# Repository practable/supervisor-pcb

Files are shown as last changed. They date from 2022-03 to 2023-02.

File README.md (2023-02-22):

# Remote Labs Supervisor PCB V1.2

## Project Brief - [Remote Labs Supervisor PCB V1.2]
Design a PCB to provide power to remote labs experiments, which involve students programming microcontrollers remotely. PCB should also provide a supervisory role, blocking actuation of experimental hardware if it is likely to cause damage to the equipment. <br> <br>

This allows students to upload their own code to a bare bones microcontroller, without risk of causing hardware damage or unsafe conditions. <br>
RemoteLabsSupervisorPCBV1 0_3DModel 

# Using Remote Labs Supervisor PCB 

_This document is intended to be a useage guide for the Remote Labs Supervisor PCB, and document the different use cases and configurations it is capable of._

For coded examples of the various features please see [PCB Unit Tests](https://github.com/ImogenWren/RemoteLabs_Supervisor_PCB/tree/main/Verification%20Tests/PCB%20Unit%20Tests), which contains
arduino code firmware used during testing all hardware features of the PCB.

For the purposes of this document, it is assumed that the Motherboard PCB is populated with both Arduino Nano IoT 33 Daughterboards __(A1 & A2)__, with shift registers installed, and NOT the bare bones SAMD21 MCU.
A seperate document will be provided for cases in which SAMD21 MCUs are mounted to the motherboard directly.

### Pin Naming and Shift Registers

_All MCU pins will be referenced by the Arduino Pin Numbers in this document. 
Additional pins are sourced via Shift Registers attached to each MCU.
Shift Register pins are labelled as Q0 - Q7.
Both MCU connections to their independent shift registers are detailed below._

MCU Pin |  Shift Register Function 	|
---		| ---						|
D8		| LATCH	(Write to Register)	|
D11		| MOSI (Data)				|
D13		| SCK						|

_Complete pinout diagrams for both MCUs and Shift Registers can be found at the bottom of this document_

### Powering the System

The System should be provided 12v DC power via the yellow XT60 connector __J3__. The system is specified to draw a maximum of ~ 8A depending on experiment configuration, ensure that power supply selected is sufficient for specific use case.

Diode D6 (Blue) will light to show correct polarity power is provided to input.
Diode D7 (Orange) will light to show 3V3 DC power is available to microcontrollers and periferal devices.

Motherboard has reverse polarity protection, however care should be taken to ensure correct orientation of power input. - NOTE: Currently missing protection diode- awaiting delivery

### Programming the MCUs

Each MCU, supervisor and student are able to be programmed via the USB connector on the daughterboard, or via UART using the 5 pin headers __J26 Student_Prog_Header__, and __J1 Super_Prog_header__.

For UART Programming, a hat is provided for raspi GPIO pins. 5 pin cable should be connected from Raspi hat to UART Programming connector on motherboard.

__The USB connectors mounted to the __Motherboard__ should not be used if Arduino Development boards are installed, and are UNTESTED for use with bare bones MCUs installed__

-----

## Use Case 1 [Spinner Experiment]

_In this configuration the following modules should be mounted to the motherboard:_

- Infineon DC Motor Control Shield - A3

_In this configuration the following external hardware should be connected as follows:_

- DC Motor, wired to the OUTER two pins on __J18 DC Motor Output__
- Optical Encoder, plugged into __J25 Optical Encoder__

### Using the DC Motor

DC Motor PWM is routed to Infineon DC Motor Controller module via the following logic:



If MOTOR_DIR_A is driven HIGH, PWM is routed from STUDENT_MOTOR_PWM or SUPERVISOR_MOTOR_PWM to MOTOR_OUT_1
If MOTOR_DIR_B is driven HIGH, PWM is routed from STUDENT_MOTOR_PWM or SUPERVISOR_MOTOR_PWM to MOTOR_OUT_2

Care must be taken to avoid driving MOTOR_DIR_A and MOTOR_DIR_B to HIGH at the same time as this will cause shoot through.

In Order to avoid shoot through condition, Student does not have direct input to MOTOR_DIR_A or MOTOR_DIR_B. These outputs are spoofed via the Supervisor MCU.

The MCU able to pass PWM signal to Motor Control Module is selected by MCU_MOTOR_SELECT pin. When HIGH - STUDENT_MOTOR_PWM is active, when LOW - SUPERVISOR_MOTOR_PWM is active.

In order to enable the DC Motor Control Module, OUT_M_ENABLE must also be set HIGH. This is routed from either MCU using the same logic as above, when MCU_MOTOR_SELECT is HIGH, ENABLE is routed from STUDENT_MOTOR_EN, when it is set LOW, ENABLE is routed from SUPERVISOR_MOTOR_EN.

M_I_SENSE_1 and M_I_SENSE_2 output is buffered and distributed to both MCUs.

### Supervisor MCU

Supervisor MCU uses the following table for DC Motor Control:

MCU 		|Pin 	| Pin Name 		| State 		| Motor Behaviour 		| Notes
---			|---	|---			|---			|---					|---
SUPERVISOR 	|D12 	|MOTOR_DIR_1	| HIGH or LOW	| Sets motor Direction	| IF(D7 == HIGH){D12 MUST = LOW)
SUPERVISOR	|D7		|MOTOR_DIR_2	| LOW or HIGH 	| Sets motor Direction 	| IF(D12 == HIGH){D7 MUST = LOW)
SUPERVISOR	|Q0		|DC_MOTOR_EN	| HIGH			| Enables DC Motor Drive|
SUPERVISOR	|Q1		|STUDENT_M_EN	| LOW			| Blocks Student Control, Enables Supervisor Control| 
SUPERVISOR	|A7		|DC_MOTOR_IS1	| ANALOG INPUT	| Current Draw and Fault Condition Detection| 
SUPERVISOR	|A6		|DC_MOTOR_IS2	| ANALOG INPUT	| Current Draw and Fault Condition Detection| 

### Student MCU

Student MCU uses the following table for DC Motor Control: *Note - Student control relys on specific pin configurations of Supervisor MCU*

MCU 		|Pin 	| Pin Name 		| State 		| Motor Behaviour 		| Notes
---			|---	|---			|---			|---					|---
STUDENT 	|D12 	|MOTOR_DIR_1	| HIGH or LOW	| Detected by Supervisor PIN A1	| IF(D7 == HIGH){D12 MUST = LOW)
STUDENT		|D7		|MOTOR_DIR_2	| LOW or HIGH 	| Detected by Supervisor PIN A0	| IF(D12 == HIGH){D7 MUST = LOW)
STUDENT		|Q0		|DC_MOTOR_EN	| HIGH			| Enables DC Motor Drive|
SUPERVISOR	|Q1		|STUDENT_M_EN	| HIGH			| Blocks Supervisor Control, Enables Student Control| 
SUPERVISOR	|A1		|STDNT_DC_M_DIR_1| DIGITAL INPUT| Detects state of Student Direction Pin and Spoofs output if logic != illegal
SUPERVISOR	|A0		|STDNT_DC_M_DIR_2| DIGITAL INPUT| Detects state of Student Direction Pin and Spoofs output if logic != illegal
SUPERVISOR 	|D12 	|MOTOR_DIR_1	| HIGH or LOW	| Sets motor Direction - Spoofed from A1	| 
SUPERVISOR	|D7		|MOTOR_DIR_2	| LOW or HIGH 	| Sets motor Direction - Spoofed from A0	| 
STUDENT		|A7		|DC_MOTOR_IS1	| ANALOG INPUT	| Current Draw and Fault Condition Detection| 
STUDENT		|A6		|DC_MOTOR_IS2	| ANALOG INPUT	| Current Draw and Fault Condition Detection| 

### Using the Optical Encoder

_Optical encoder signals are buffered and provided to both MCUs simaltaniously, therefore getting useful data from Optical Encoder is the same process for both MCUs_

MCUs use the following table for Optical Encoder detection:

MCU 		|Pin 	| Pin Name 		| State 								| Notes
---			|---	|---			|---									|---
Both	 	|D2 	|ENCODER_B		| EXTERNAL INTERRUPT / DIGITAL INPUT	| For best performance, External Interrupt used for edge detection of Encoder waveform
Both		|D3		|ENCODER_A		| EXTERNAL INTERRUPT / DIGITAL INPUT 	| Alternative pin for External Interrupt.
Both		|D4		|ENCODER_INDEX	| DIGITAL INPUT							| Used to track center detent of optical encoder (Untested in software)

-----

## Use Case 2 [Governer Experiment]

In this configuration the following modules should be mounted to the motherboard:

- Infineon DC Motor Control Shield 	- A3
- DRV8825 Stepper Motor Driver		- A4

___DC Motor & Optical Encoder are accessed as Use Case 1 above___

In this configuration the following external hardware should be connected as follows:

- DC Motor, wired to the OUTER two pins on __J18 DC Motor Output__
- Stepper Motor, plugged into __J19 Stepper Motor Output__
- Optical Encoder, plugged into __J25 Optical Encoder__
- Limit Switch, plugged into __J23 limit_switch_A__

### Using the Stepper Motor

Stepper Motor Driver inputs are routed via the following logic:



When MCU_STEP_SELECT is HIGH, inputs are routed from STUDENT MCU. When MCU_STEP_SELECT is LOW, inputs are routed from SUPERVISOR MCU.

STEPP_EN is driven from Supervisor MCU Only, however does not seem to have any effect on stepper motor function. - Requires further investigation.

STEPPR_FAULT output is buffered and distributed to both MCUs.

LIMIT_1 Limit switch input is buffered and distributed to both MCUs.

### Supervisor MCU

Supervisor MCU uses the following table for Stepper Motor Control:

MCU 		|Pin 	| Pin Name 		| State 		| Motor Behaviour 									| Notes
---			|---	|---			|---			|---												|---
SUPERVISOR 	|D6 	|STEPP_STEP		| PULSE			| Motor advances 1 step per pulse					| 
SUPERVISOR	|Q2		|STUDENT_STEP_EN| LOW			| Blocks Student Control, Enables Supervisor Control| 
SUPERVISOR	|Q4		|STEPP_DIR		| HIGH or LOW	| Sets Stepper Motor Direction						|
SUPERVISOR	|Q5		|STEPP_SLP		| HIGH or LOW	| Enables and Sleeps motor to avoid overheating 	| MUST BE HIGH? to enable					| 
SUPERVISOR	|Q6		|STEPP_RST		| HIGH or LOW	| Resets controller board after fault condition 	| MUST BE HIGH? to enable					| 
SUPERVISOR	|Q7		|STEPP_EN		| HIGH or LOW	| Enables motor driver board						| NO DECERNABLE EFFECT? - Needs Testing		| 
SUPERVISOR	|A5		|STEPP_FLT		| DIGITAL INPUT	| Fault reporting from Stepper Control daughterboard| HIGH = NO FAULT, LOW = FAULT 				| 
SUPERVISOR	|A4		|LIMIT_1		| DIGITAL INPUT	| Limit Switch Detection.							| LOW = Switch Pressed 						| 

### Student MCU

Student MCU uses the following table for Stepper Motor Control: *Note - Student control relys on specific pin configurations of Supervisor MCU*

MCU 		|Pin 	| Pin Name 		| State 		| Motor Behaviour 									| Notes
---			|---	|---			|---			|---												|---
STUDENT 	|D6 	|STEPP_STEP		| PULSE			| Motor advances 1 step per pulse					| 
SUPERVISOR	|Q2		|STUDENT_STEP_EN| HIGH			| Enables Student Control, Blocks Supervisor Control| 
STUDENT 	|Q4		|STEPP_DIR		| HIGH or LOW	| Sets Stepper Motor Direction						|
STUDENT		|Q5		|STEPP_SLP		| HIGH or LOW	| Enables and Sleeps motor to avoid overheating 	| MUST BE HIGH? to enable					| 
STUDENT		|Q6		|STEPP_RST		| HIGH or LOW	| Resets controller board after fault condition 	| MUST BE HIGH? to enable					| 
SUPERVISOR	|Q7		|STEPP_EN		| HIGH or LOW	| Enables motor driver board						| NO DECERNABLE EFFECT? - Needs Testing		| 
STUDENT		|A5		|STEPP_FLT		| DIGITAL INPUT	| Fault reporting from Stepper Control daughterboard| HIGH = NO FAULT, LOW = FAULT 				| 
STUDENT		|A4		|LIMIT_1		| DIGITAL INPUT	| Limit Switch Detection.							| LOW = Switch Pressed 						|

#### Additional Stepper Motor Functions

SW1 - Stepper Mode Dipswitches set number of steps per revolution. If UNPOPULATED setting is at MAX RESOLUTION. (1, 1, 1 ) logic for MODE inputs.

-----

## Use Case 3 [Digger Experiment]

In this configuration the following modules should be mounted to the motherboard:

- Infineon DC Motor Control Shield 	- A3

___DC Motor & Optical Encoder are accessed as Use Case 1 above___

In this configuration the following external hardware should be connected as follows:

- DC Motor, wired to the OUTER two pins on __J18 DC Motor Output__
- Optical Encoder, plugged into __J25 Optical Encoder__
- Limit Switch, plugged into __J23 limit_switch_A__
- Servo, plugged into __J20 Servo_A__

In this use case, supervisor must calibrate and track the position of DC motor to avoid equipment collision with self. 

### Supervisor MCU

Supervisor has ultimate control of the Servo PPM output.

Supervisor MCU uses the following table for Servo Motor Control:

MCU 		|Pin 	| Pin Name 		| State 		| Motor Behaviour 									| Notes
---			|---	|---			|---			|---												|---
SUPERVISOR 	|D9 	|SERVO_1		| PPM Output	| PPM Standard sets Servo Position					| 

### Student MCU

Student MCU has no direct output to servo_1, instead supervisor must spoof and constrain output;
given either a PWM signal, or PPM signal from the Student, applied to __Pin A2__ of the supervisorU MCU.

Student MCU uses the following table for Servo Motor Control: *Note - Student control relys on specific pin configurations of Supervisor MCU*

MCU 		|Pin 	| Pin Name 		| State 		| Motor Behaviour 									| Notes
---			|---	|---			|---			|---												|---
STUDENT 	|D9 	|SERVO_1		| PPM or PWM Output	| PPM/PWM used to infer desired position of servo	| 
SUPERVISOR	|A2		|STDNT_SRVO_RX_1| ANALOG INPUT or EXTERNAL INTERRUPT	| Detects infered desired position for servo| 
SUPERVISOR 	|D9 	|SERVO_1		| PPM Output	| PPM Standard sets Servo Position					| 

-----

## Use Case 4 [Pendulum Experiment]

*NOTE: USE CASE UNTESTED*

In this configuration the following modules should be mounted to the motherboard:

- Remote Labs Pendulum PCB Daughterboard - A3

In this configuration the following external hardware should be connected as follows:

- Pendulum Driver, wired to the OUTER two pins on __J18 DC Motor Output__
- Optical Encoder, plugged into __J25 Optical Encoder__

### Supervisor MCU

Supervisor MCU uses the following table for Pendulum Control:

MCU 		|Pin 	| Pin Name 		|Pendulum PCB Pin Name	| State 		| Pendulum Behaviour 	| Notes
---			|---	|---			|---					|---			|---					|---
SUPERVISOR 	|Q0		|DC_MOTOR_EN	| ENABLE	| DIGTAL OUTPUT	| Drive	 |Tried to avoid this being on a shift register - failed can it be moved to another pin? User Thermo A3, and enable
SUPERVISOR 	|D6		|STEPP_STEP		| PENDULUM_PIN_1		| DIGTAL OUTPUT	| Load					|  
SUPERVISOR 	|D12	|DC_MOTOR_DIR_1	| PENDULUM_PIN_7		| DIGTAL OUTPUT	| LED_1 Control			| 	
SUPERVISOR 	|D7		|DC_MOTOR_DIR_2	| PENDULUM_PIN_8		| DIGTAL OUTPUT	| LED_2 Control			| 
SUPERVISOR 	|D9		|SERVO_1		| PENDULUM_PIN_6		| DIGTAL OUTPUT	| LED_3 Control			| 
SUPERVISOR 	|Q1		|STUDENT_M_EN	| PENDULUM_PIN_2		| LOW			| Blocks Student Control, Enables Supervisor Control |
SUPERVISOR	|A7		|DC_MOTOR_IS1	| I_SENSE_1				| ANALOG INPUT	| Current Draw and Fault Condition Detection|  Check which way around these are
SUPERVISOR	|A6		|DC_MOTOR_IS2	| I_SENSE_2				| DIGITAL INPUT	| Current SIGN reporting (+/-)| HIGH = Positive Current, LOW = Negative Current

### Student MCU

Student MCU uses the following table for Stepper Motor Control: *Note - Student control relys on specific pin configurations of Supervisor MCU*

MCU 		|Pin 	| Pin Name 		|Pendulum PCB Pin Name	| State 		| Pendulum Behaviour 	| Notes
---			|---	|---			|---					|---			|---					|---
STUDENT 	|Q0		|DC_MOTOR_EN	| ENABLE	| DIGTAL OUTPUT	| Drive	 |Tried to avoid this being on a shift register - failed can it be moved to another pin? User Thermo A3, and external enable
STUDENT 	|D6		|STEPP_STEP		| PENDULUM_PIN_1		| DIGTAL OUTPUT	| Load					|  
STUDENT  	|A0		|SPARE_0		| PENDULUM_PIN_3		| DIGTAL OUTPUT	| LED_1 Control			| 	
STUDENT  	|A1		|SPARE_1 		| PENDULUM_PIN_4		| DIGTAL OUTPUT	| LED_2 Control			| 
STUDENT  	|A2		|SPARE_2		| PENDULUM_PIN_5		| DIGTAL OUTPUT	| LED_3 Control			| 
SUPERVISOR 	|Q1		|STUDENT_M_EN	| PENDULUM_PIN_2		| HIGH			| Enables Student Control, Blocks Supervisor Control |
STUDENT		|A7		|DC_MOTOR_IS1	| I_SENSE_1				| ANALOG INPUT	| Current Draw and Fault Condition Detection|  Check which way around these are
STUDENT		|A6		|DC_MOTOR_IS2	| I_SENSE_2				| DIGITAL INPUT	| Current SIGN reporting (+/-)| HIGH = Positive Current, LOW = Negative Current

-----

## Additional Features

### WS2812 LEDs

To use WS2812 LED strips with any configuration, the following external hardware should be connected as follows:

- WS2821B LED Strip, connected to __J24 WS2812B LEDs__

__Supervisor MCU__ uses the following table for WS2812B LED Control.

MCU 		|Pin 	| Pin Name 		| State 		| Use			 				| Notes
---			|---	|---			|---			|---							|---
SUPERVISOR 	|D5 	|PIXEL_DATA		| DIGITAL OUTPUT| Sets LED Colour & Brightness	|
SUPERVISOR	|Q3		|STUDENT_PIXEL_EN| LOW			| Blocks Student Control, Enables Supervisor Control		|

__Student MCU__ uses the following table for WS2812B LED Control.: *Note - Student control relys on specific pin configurations of Supervisor MCU*

MCU 		|Pin 	| Pin Name 		| State 		| Use			 				| Notes
---			|---	|---			|---			|---							|---
STUDENT		|D5 	|PIXEL_DATA		| DIGITAL OUTPUT| Sets LED Colour & Brightness	|
SUPERVISOR	|Q3		|STUDENT_PIXEL_EN| HIGH			| Enables Student Control, Blocks Supervisor Control		|

### Power Output Connectors

| Voltage/Bus 		| Purpose/Name	| Component Number 	| Connector Type 	| Current Considerations 	|
|---				|---			|---				|---				|---						|
| 12V				| 12V_DC		|		J30			| Screw Terminal	| Unregulated ~8A Max(For entire Bus)|
| 12V				| Strip Lighting| 		J4			| Molex				| Unregulated ~8A Max(For entire Bus)|
| 12V       		| DC MOTOR PWR	|		J16			| Screw Terminal	| Unregulated ~8A Max(For entire Bus)|
| 5V_DC_LED			| 5V_DC_LED		| 		J6			| Screw Terminal	| 1A Total. Regulated	|
| 5V_DC_RPI			| 5V_DC Spare	| 		J31			| Screw Terminal	| 2.5A Total. Regulated	|
| 5V_DC_RPI			| USB Power		| 		J5			| USB A Socket x2	| 2.5A Total. Regulated	|

#### Additional Voltage Bus Connections

Additional headers have been provided for:
- 3V3 DC Power Output (1A Max)
- 5V DC Digital Power Output (2 - 2.5A Max, including USB Socket)
- 5V DC Servo Power Output (1A Max)
- 12V DC Bus (Unregulated - 6A Max)

These are intended for future use, fault finding or reconfirging PCBs to perform tasks outside of the specified use cases.

### Thermocouple

__Currently Unavailable due to parts shortages__

To use Thermocouple Input with any configuration, the following external hardware should be connected as follows:

- K-Type Thermocouple, connected to __J22 Thermocouple__ connector.

__Thermocouple input __J22 Thermocouple__ requires IC __U19 AD8497__ To be populated. (UNTESTED)__

Analog voltage is buffered and distributed to both MCUs, __Pin A3__

## Pinout Diagrams

_MCU and Shift Register Pinout diagrams_

##### Supervisor MCU



##### Student MCU



## CAD Renders

RemoteLabs Supervisor PCBV1 0 CAD Design
RemoteLabsSupervisorPCBV1 0_3DModel_3


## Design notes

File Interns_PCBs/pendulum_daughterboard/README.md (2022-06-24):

# Pendulum Driver Daughterboard

The task is to design and fabricate a drop in replacement for the motor driver board on the new remote labs PCB. The original daughterboard is the Infineon motor control shield:
  https://uk.rs-online.com/web/p/shields-for-arduino/

The new PCB will be driving the pendulum experiment, the circuit and experiment is documented in this github repo:
https://github.com/practable/penduino

Pendulum Driver Origional Circuit

RL supervisor PCB repo found at:
https://github.com/ImogenWren/RemoteLabs_Supervisor_PCB

### Schematic Showing connections to motherboard
 Infineon Motor Driver Connections to motherboard

I have created a folder for the pendulum daughterboard, if you could keep all the KiCAD files and any notes you make in this folder. Part of the reasoning of this project is “showing our working” so documenting any design decisions you make, current draw calculations, trace sizes etc would be valuable.

The new daughterboard needs to fit into the slot for the old daughterboard, and must match its pinout. We have 3 digital inputs available to the daughterboard, ENABLE, IN_1 and IN_2 and 2 Analog outputs from the daughterboard. The analog outputs go through a set of buffers to feed the ADC pins on each MCU, and both have a 470r resistor to GND. 

On the schematic it shows 4 digital inputs, so I would have a quick chat with Tim Drysdale (CCed In) and ask him if we can tie the two LEDs to the drive and the load pin. This means we would have 2 digital inputs, and one spare. Don’t worry about the encoder as that plugs directly into the motherboard and doesn’t need any additional work.

I don’t know if it is required, but it might be worthwhile thinking about adding some kind of current sensing to the daughterboard which can be output on the analog pins. This could be via a current sense IC, or some other method. It would likely need to measure current through the coil in both directions, but this is a stretch goal. The important part is just replicating the function of the existing circuit. Whatever method is chosen, make sure that the parts to complete are available and in stock from UK suppliers.

Power input into the daughterboard – unfortunately I didn’t think of putting 5v on any of the spare pins, however there is a 5v header on the motherboard, so we will run a wire from here into a large 5v Vin pin on your daughterboard. The coil connections will come out on 2 large pads, like the motor driver board and this will be wired to the screw terminals on the motherboard. These are shown as dotted lines on the picture above.

Ideally this should be a 2 layer board to allow us to fabricate a prototype in house.

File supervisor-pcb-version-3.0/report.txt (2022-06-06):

Info: Processing symbol 'A1:Module:Arduino_Nano'.
Info: Processing symbol 'A2:Module:Arduino_Nano'.
Info: Processing symbol 'A3:Module:Infineon Motor Sheild hiddenPins'.
Info: Processing symbol 'A4:Module:DRV8825 Stepper Motor Module'.
Info: Processing symbol 'A5:Module:LM2596S DC-DC Module'.
Info: Processing symbol 'C1:Capacitor_SMD:C_0805_2012Metric_Pad1.18x1.45mm_HandSolder'.
Info: Processing symbol 'C1A1:Capacitor_SMD:C_0805_2012Metric_Pad1.18x1.45mm_HandSolder'.
Info: Processing symbol 'C1B1:Capacitor_SMD:C_0805_2012Metric_Pad1.18x1.45mm_HandSolder'.
Info: Processing symbol 'C2:Capacitor_SMD:C_0805_2012Metric_Pad1.18x1.45mm_HandSolder'.
Info: Processing symbol 'C2A1:Capacitor_SMD:C_0805_2012Metric_Pad1.18x1.45mm_HandSolder'.
Info: Processing symbol 'C2B1:Capacitor_SMD:C_0805_2012Metric_Pad1.18x1.45mm_HandSolder'.
Info: Processing symbol 'C3:Capacitor_SMD:C_0805_2012Metric_Pad1.18x1.45mm_HandSolder'.
Info: Processing symbol 'C4:Capacitor_SMD:C_0805_2012Metric_Pad1.18x1.45mm_HandSolder'.
Info: Processing symbol 'C5:Capacitor_SMD:C_0805_2012Metric_Pad1.18x1.45mm_HandSolder'.
Info: Processing symbol 'C6:Capacitor_SMD:C_0805_2012Metric_Pad1.18x1.45mm_HandSolder'.
Info: Processing symbol 'C7:Capacitor_Tantalum_SMD:CP_EIA-2012-12_Kemet-R_Pad1.30x1.05mm_HandSolder'.
Info: Processing symbol 'C8:Capacitor_SMD:C_0805_2012Metric_Pad1.18x1.45mm_HandSolder'.
Info: Processing symbol 'C9:Capacitor_SMD:C_0805_2012Metric_Pad1.18x1.45mm_HandSolder'.
Info: Processing symbol 'C10:Capacitor_SMD:C_0805_2012Metric_Pad1.18x1.45mm_HandSolder'.
Info: Processing symbol 'C11:Capacitor_SMD:C_0805_2012Metric_Pad1.18x1.45mm_HandSolder'.
Info: Processing symbol 'C12:Capacitor_SMD:C_0805_2012Metric_Pad1.18x1.45mm_HandSolder'.
Info: Processing symbol 'C13:Capacitor_SMD:C_0805_2012Metric_Pad1.18x1.45mm_HandSolder'.
Info: Processing symbol 'C14:Capacitor_SMD:C_0805_2012Metric_Pad1.18x1.45mm_HandSolder'.
Info: Processing symbol 'C15:Capacitor_SMD:C_0805_2012Metric_Pad1.18x1.45mm_HandSolder'.
Info: Processing symbol 'C16:Capacitor_SMD:C_0805_2012Metric_Pad1.18x1.45mm_HandSolder'.
Info: Processing symbol 'C17:Capacitor_Tantalum_SMD:CP_EIA-2012-12_Kemet-R_Pad1.30x1.05mm_HandSolder'.
Info: Processing symbol 'C18:Capacitor_SMD:C_0805_2012Metric_Pad1.18x1.45mm_HandSolder'.
Info: Processing symbol 'C19:Capacitor_SMD:C_0805_2012Metric_Pad1.18x1.45mm_HandSolder'.
Info: Processing symbol 'C20:Capacitor_SMD:C_0805_2012Metric_Pad1.18x1.45mm_HandSolder'.
Info: Processing symbol 'C21:Capacitor_SMD:C_0805_2012Metric_Pad1.18x1.45mm_HandSolder'.
Info: Processing symbol 'C22:Capacitor_SMD:C_0805_2012Metric_Pad1.18x1.45mm_HandSolder'.
Info: Processing symbol 'C23:Capacitor_SMD:C_0805_2012Metric_Pad1.18x1.45mm_HandSolder'.
Info: Processing symbol 'C24:Capacitor_SMD:C_0805_2012Metric_Pad1.18x1.45mm_HandSolder'.
Info: Processing symbol 'C25:Capacitor_SMD:C_0805_2012Metric_Pad1.18x1.45mm_HandSolder'.
Info: Processing symbol 'C26:Capacitor_SMD:C_0805_2012Metric_Pad1.18x1.45mm_HandSolder'.
Info: Processing symbol 'C27:Capacitor_SMD:C_0805_2012Metric_Pad1.18x1.45mm_HandSolder'.
Info: Processing symbol 'C28:Capacitor_SMD:C_0805_2012Metric_Pad1.18x1.45mm_HandSolder'.
Info: Processing symbol 'C29:Capacitor_SMD:C_0805_2012Metric_Pad1.18x1.45mm_HandSolder'.
Info: Processing symbol 'C30:Capacitor_SMD:C_0805_2012Metric_Pad1.18x1.45mm_HandSolder'.
Info: Processing symbol 'C31:Capacitor_SMD:C_0805_2012Metric_Pad1.18x1.45mm_HandSolder'.
Info: Processing symbol 'C32:Capacitor_SMD:C_0805_2012Metric_Pad1.18x1.45mm_HandSolder'.
Info: Processing symbol 'C33:Capacitor_SMD:C_0805_2012Metric_Pad1.18x1.45mm_HandSolder'.
Info: Processing symbol 'C34:Capacitor_SMD:C_0805_2012Metric_Pad1.18x1.45mm_HandSolder'.
Info: Processing symbol 'C35:Capacitor_SMD:C_0805_2012Metric_Pad1.18x1.45mm_HandSolder'.
Info: Processing symbol 'C36:Capacitor_SMD:C_0805_2012Metric_Pad1.18x1.45mm_HandSolder'.
Info: Processing symbol 'C38:Capacitor_SMD:C_0805_2012Metric_Pad1.18x1.45mm_HandSolder'.
Info: Processing symbol 'C39:Capacitor_SMD:C_0805_2012Metric_Pad1.18x1.45mm_HandSolder'.
Info: Processing symbol 'C40:Capacitor_SMD:C_0805_2012Metric_Pad1.18x1.45mm_HandSolder'.
Info: Processing symbol 'C41:Capacitor_SMD:C_0805_2012Metric_Pad1.18x1.45mm_HandSolder'.
Info: Processing symbol 'C42:Capacitor_SMD:C_0805_2012Metric_Pad1.18x1.45mm_HandSolder'.
Info: Processing symbol 'C43:Capacitor_SMD:C_0805_2012Metric_Pad1.18x1.45mm_HandSolder'.
Info: Processing symbol 'D1:Diode_SMD:D_MiniMELF'.
Info: Processing symbol 'D2:Diode_SMD:Nexperia_CFP3_SOD-123W'.
Info: Processing symbol 'D3:Package_TO_SOT_SMD:SOT-143'.
Info: Processing symbol 'D4:Package_TO_SOT_SMD:SOT-143'.
Info: Processing symbol 'D5:Diode_SMD:Nexperia_CFP3_SOD-123W'.
Info: Processing symbol 'D6:Diode_SMD:D_0805_2012Metric_Pad1.15x1.40mm_HandSolder'.
Info: Processing symbol 'D7:Diode_SMD:D_0805_2012Metric_Pad1.15x1.40mm_HandSolder'.
Info: Processing symbol 'D8:Diode_SMD:D_0805_2012Metric_Pad1.15x1.40mm_HandSolder'.
Info: Processing symbol 'R19:Resistor_SMD:R_0805_2012Metric_Pad1.20x1.40mm_HandSolder'.
Info: Processing symbol 'D9:Diode_SMD:D_0805_2012Metric_Pad1.15x1.40mm_HandSolder'.
Info: Processing symbol 'R20:Resistor_SMD:R_0805_2012Metric_Pad1.20x1.40mm_HandSolder'.
Info: Processing symbol 'EC1:Capacitor_SMD:CP_Elec_4x5.4'.
Info: Processing symbol 'EC2:Capacitor_SMD:CP_Elec_4x5.4'.
Info: Processing symbol 'EC3:Capacitor_SMD:CP_Elec_4x5.4'.
Info: Processing symbol 'EC4:Capacitor_SMD:CP_Elec_4x5.4'.
Info: Processing symbol 'EC5:Capacitor_SMD:CP_Elec_4x5.4'.
Info: Processing symbol 'EC6:Capacitor_SMD:CP_Elec_4x5.4'.
Info: Processing symbol 'EC7:Capacitor_SMD:CP_Elec_4x5.4'.
Info: Processing symbol 'EC8:Capacitor_SMD:CP_Elec_4x5.4'.
Info: Processing symbol 'EC9:Capacitor_SMD:CP_Elec_6.3x7.7'.
Info: Processing symbol 'EC10:Capacitor_SMD:CP_Elec_6.3x7.7'.
Info: Processing symbol 'EC11:Capacitor_SMD:CP_Elec_6.3x7.7'.
Info: Processing symbol 'EC12:Capacitor_SMD:CP_Elec_6.3x7.7'.
Info: Processing symbol 'F1:Fuse:Fuseholder_Cylinder-5x20mm_Stelvio-Kontek_PTF78_Horizontal_Open'.
Info: Processing symbol 'F2:Fuse:Fuseholder_Cylinder-5x20mm_Stelvio-Kontek_PTF78_Horizontal_Open'.
Info: Processing symbol 'FB1:Inductor_SMD:L_0805_2012Metric_Pad1.05x1.20mm_HandSolder'.
Info: Processing symbol 'FB2:Inductor_SMD:L_0805_2012Metric_Pad1.05x1.20mm_HandSolder'.
Info: Processing symbol 'H1:MountingHole:MountingHole_3.2mm_M3_Pad_Via'.
Info: Processing symbol 'R21:Resistor_SMD:R_0805_2012Metric_Pad1.20x1.40mm_HandSolder'.
Info: Processing symbol 'R22:Resistor_SMD:R_0805_2012Metric_Pad1.20x1.40mm_HandSolder'.
Info: Processing symbol 'R23:Resistor_SMD:R_0805_2012Metric_Pad1.20x1.40mm_HandSolder'.
Info: Processing symbol 'R24:Resistor_SMD:R_0805_2012Metric_Pad1.20x1.40mm_HandSolder'.
Info: Processing symbol 'R25:Resistor_SMD:R_0805_2012Metric_Pad1.20x1.40mm_HandSolder'.
Info: Processing symbol 'R26:Resistor_SMD:R_0805_2012Metric_Pad1.20x1.40mm_HandSolder'.
Info: Processing symbol 'R27:Resistor_SMD:R_0805_2012Metric_Pad1.20x1.40mm_HandSolder'.
Info: Processing symbol 'R28:Resistor_SMD:R_0805_2012Metric_Pad1.20x1.40mm_HandSolder'.
Info: Processing symbol 'R29:Resistor_SMD:R_0805_2012Metric_Pad1.20x1.40mm_HandSolder'.
Info: Processing symbol 'H2:MountingHole:MountingHole_3.2mm_M3_Pad_Via'.
Info: Processing symbol 'R30:Resistor_SMD:R_0805_2012Metric_Pad1.20x1.40mm_HandSolder'.
Info: Processing symbol 'R31:Resistor_SMD:R_0805_2012Metric_Pad1.20x1.40mm_HandSolder'.
Info: Processing symbol 'R32:Resistor_SMD:R_0805_2012Metric_Pad1.20x1.40mm_HandSolder'.
Info: Processing symbol 'R33:Resistor_SMD:R_0805_2012Metric_Pad1.20x1.40mm_HandSolder'.
Info: Processing symbol 'R34:Resistor_SMD:R_0805_2012Metric_Pad1.20x1.40mm_HandSolder'.
Info: Processing symbol 'R35:Resistor_SMD:R_0805_2012Metric_Pad1.20x1.40mm_HandSolder'.
Info: Processing symbol 'R36:Resistor_SMD:R_0805_2012Metric_Pad1.20x1.40mm_HandSolder'.
Info: Processing symbol 'R37:Resistor_SMD:R_0805_2012Metric_Pad1.20x1.40mm_HandSolder'.
Info: Processing symbol 'R39:Resistor_SMD:R_0805_2012Metric_Pad1.20x1.40mm_HandSolder'.
Info: Processing symbol 'H3:MountingHole:MountingHole_3.2mm_M3_Pad_Via'.
Info: Processing symbol 'R40:Resistor_SMD:R_0805_2012Metric_Pad1.20x1.40mm_HandSolder'.
Info: Processing symbol 'J25:Connector_Molex:Molex_KK-254_AE-6410-05A_1x05_P2.54mm_Vertical'.
Info: Processing symbol 'R41:Resistor_SMD:R_0805_2012Metric_Pad1.20x1.40mm_HandSolder'.
Info: Processing symbol 'SW1:Button_Switch_SMD:SW_DIP_SPSTx03_Slide_6.7x9.18mm_W6.73mm_P2.54mm_LowProfile_JPin'.
Info: Processing symbol 'SW2:Button_Switch_SMD:SW_Push_1P1T_NO_CK_KSC6xxJ'.
Info: Processing symbol 'SW3:Button_Switch_SMD:SW_Push_1P1T_NO_CK_KSC6xxJ'.
Info: Processing symbol 'U1:Converter_DCDC:Converter_DCDC_RECOM_R-78E-0.5_THT'.
Info: Processing symbol 'U2:Package_TO_SOT_SMD:SOT-23-5_HandSoldering'.
Info: Processing symbol 'U3:Package_TO_SOT_SMD:SOT-223-3_TabPin2'.
Info: Processing symbol 'H4:MountingHole:MountingHole_3.2mm_M3_Pad_Via'.
Info: Processing symbol 'U4:Package_DFN_QFN:QFN-48-1EP_7x7mm_P0.5mm_EP5.15x5.15mm'.
Info: Processing symbol 'U5:Package_SO:SOIC-16_3.9x9.9mm_P1.27mm'.
Info: Processing symbol 'U6:Package_DFN_QFN:QFN-48-1EP_7x7mm_P0.5mm_EP5.15x5.15mm'.
Info: Processing symbol 'U7:Package_SO:SOIC-16_3.9x9.9mm_P1.27mm'.
Info: Processing symbol 'U8:Package_SO:SOIC-14_3.9x8.7mm_P1.27mm'.
Info: Processing symbol 'U9:Package_SO:SOIC-14_3.9x8.7mm_P1.27mm'.
Info: Processing symbol 'U10:Package_SO:SOIC-14_3.9x8.7mm_P1.27mm'.
Info: Processing symbol 'U11:Package_SO:SOIC-14_3.9x8.7mm_P1.27mm'.
Info: Processing symbol 'U12:Package_SO:SOIC-14_3.9x8.7mm_P1.27mm'.
Info: Processing symbol 'H5:MountingHole:MountingHole_3.2mm_M3_Pad_Via'.
Info: Processing symbol 'U13:Package_SO:SOIC-14_3.9x8.7mm_P1.27mm'.
Info: Processing symbol 'U14:Package_SO:SOIC-14_3.9x8.7mm_P1.27mm'.
Info: Processing symbol 'U15:Package_SO:SOIC-14_3.9x8.7mm_P1.27mm'.
Info: Processing symbol 'U16:Package_SO:SOIC-14_3.9x8.7mm_P1.27mm'.
Info: Processing symbol 'U17:Package_SO:SOIC-14_3.9x8.7mm_P1.27mm'.
Info: Processing symbol 'U18:Converter_DCDC:Converter_DCDC_RECOM_R-78E-0.5_THT'.
Info: Processing symbol 'U19:Package_SO:MSOP-8_3x3mm_P0.65mm'.
Info: Processing symbol 'U20:Package_SO:SOIC-14_3.9x8.7mm_P1.27mm'.
Info: Processing symbol 'U21:Package_SO:SOIC-14_3.9x8.7mm_P1.27mm'.
Info: Processing symbol 'H6:MountingHole:MountingHole_3.2mm_M3_Pad_Via'.
Info: Processing symbol 'U22:Package_SO:SOIC-14_3.9x8.7mm_P1.27mm'.
Info: Processing symbol 'U23:Package_TO_SOT_SMD:SOT-23-5_HandSoldering'.
Info: Processing symbol 'X1:Oscillator:Oscillator_SMD_Abracon_ASE-4Pin_3.2x2.5mm'.
Info: Processing symbol 'X2:Oscillator:Oscillator_SMD_Abracon_ASE-4Pin_3.2x2.5mm'.
Info: Processing symbol 'R38:Resistor_SMD:R_0805_2012Metric_Pad1.20x1.40mm_HandSolder'.
Info: Processing symbol 'J1:Connector_Molex:Molex_KK-254_AE-6410-05A_1x05_P2.54mm_Vertical'.
Info: Processing symbol 'J2:Connector_Molex:Molex_KK-254_AE-6410-03A_1x03_P2.54mm_Vertical'.
Info: Processing symbol 'J3:Connector_AMASS:AMASS_XT60PW-M'.
Info: Processing symbol 'J4:Connector_Molex:Molex_KK-254_AE-6410-02A_1x02_P2.54mm_Vertical'.
Info: Processing symbol 'J5:Connector_USB:USB_A_Wuerth_61400826021_Horizontal_Stacked'.
Info: Processing symbol 'J6:TerminalBlock:TerminalBlock_Altech_AK300-2_P5.00mm'.
Info: Processing symbol 'J7:Connector_USB:USB_Mini-B_Lumberg_2486_01_Horizontal'.
Info: Processing symbol 'J8:Connector_PinHeader_2.54mm:PinHeader_1x08_P2.54mm_Vertical'.
Info: Processing symbol 'J9:Connector_PinHeader_2.54mm:PinHeader_1x04_P2.54mm_Vertical'.
Info: Processing symbol 'J10:Connector_PinHeader_2.54mm:PinHeader_1x08_P2.54mm_Vertical'.
Info: Processing symbol 'J11:Connector_PinHeader_2.54mm:PinHeader_1x03_P2.54mm_Vertical'.
Info: Processing symbol 'J12:Connector_PinHeader_2.54mm:PinHeader_1x08_P2.54mm_Vertical'.
Info: Processing symbol 'J13:Connector_USB:USB_Mini-B_Lumberg_2486_01_Horizontal'.
Info: Processing symbol 'J14:Connector_PinHeader_2.54mm:PinHeader_1x08_P2.54mm_Vertical'.
Info: Processing symbol 'J15:Connector_PinHeader_2.54mm:PinHeader_1x03_P2.54mm_Vertical'.
Info: Processing symbol 'J16:TerminalBlock:TerminalBlock_Altech_AK300-2_P5.00mm'.
Info: Processing symbol 'J17:TerminalBlock:TerminalBlock_Altech_AK300-3_P5.00mm'.
Info: Processing symbol 'J18:TerminalBlock:TerminalBlock_Altech_AK300-3_P5.00mm'.
Info: Processing symbol 'J19:Connector_JST:JST_XH_B4B-XH-A_1x04_P2.50mm_Vertical'.
Info: Processing symbol 'J20:Connector_PinHeader_2.54mm:PinHeader_1x03_P2.54mm_Vertical'.
Info: Processing symbol 'J21:Connector_PinHeader_2.54mm:PinHeader_1x03_P2.54mm_Vertical'.
Info: Processing symbol 'J22:TerminalBlock:TerminalBlock_Altech_AK300-2_P5.00mm'.
Info: Processing symbol 'J23:Connector_Molex:Molex_KK-254_AE-6410-02A_1x02_P2.54mm_Vertical'.
Info: Processing symbol 'J24:Connector_Molex:Molex_KK-254_AE-6410-02A_1x02_P2.54mm_Vertical'.
Info: Processing symbol 'J26:Connector_Molex:Molex_KK-254_AE-6410-05A_1x05_P2.54mm_Vertical'.
Info: Processing symbol 'J27:Connector_PinHeader_2.54mm:PinHeader_1x03_P2.54mm_Vertical'.
Info: Processing symbol 'J28:Connector_PinHeader_1.27mm:PinHeader_1x01_P1.27mm_Vertical'.
Info: Processing symbol 'J29:Connector_PinHeader_2.54mm:PinHeader_1x03_P2.54mm_Vertical'.
Info: Processing symbol 'J30:TerminalBlock:TerminalBlock_Altech_AK300-2_P5.00mm'.
Info: Processing symbol 'J31:TerminalBlock:TerminalBlock_Altech_AK300-2_P5.00mm'.
Info: Processing symbol 'J32:Connector_PinHeader_1.27mm:PinHeader_1x10_P1.27mm_Vertical'.
Info: Processing symbol 'J33:Connector_PinHeader_2.54mm:PinHeader_1x05_P2.54mm_Vertical'.
Info: Processing symbol 'J34:Connector_PinHeader_2.54mm:PinHeader_1x05_P2.54mm_Vertical'.
Info: Processing symbol 'J35:Connector_PinHeader_2.54mm:PinHeader_1x05_P2.54mm_Vertical'.
Info: Processing symbol 'J36:Connector_PinHeader_2.54mm:PinHeader_1x05_P2.54mm_Vertical'.
Info: Processing symbol 'JP1:Jumper:SolderJumper-3_P1.3mm_Bridged12_RoundedPad1.0x1.5mm'.
Info: Processing symbol 'JP2:Jumper:SolderJumper-3_P1.3mm_Bridged12_RoundedPad1.0x1.5mm'.
Info: Processing symbol 'JP3:000_Connectors_Immo:SolderJumper-3_P1.3mm_Bridged12_RoundedPad1.0x1.5mm_NumberLabels'.
Info: Processing symbol 'JP4:000_Connectors_Immo:SolderJumper-3_P1.3mm_Bridged12_RoundedPad1.0x1.5mm_NumberLabels'.
Info: Processing symbol 'JP6:000_Connectors_Immo:SolderJumper-3_P1.3mm_Bridged12_RoundedPad1.0x1.5mm_NumberLabels'.
Info: Processing symbol 'JP7:000_Connectors_Immo:SolderJumper-3_P1.3mm_Bridged12_RoundedPad1.0x1.5mm_NumberLabels'.
Info: Processing symbol 'JP9:000_Connectors_Immo:SolderJumper-2_P1.3mm_Open_Pad1.0x1.5mm'.
Info: Processing symbol 'JP10:000_Connectors_Immo:SolderJumper-2_P1.3mm_Open_Pad1.0x1.5mm'.
Info: Processing symbol 'NT1:NetTie:NetTie-2_SMD_Pad2.0mm'.
Info: Processing symbol 'NT2:NetTie:NetTie-2_SMD_Pad0.5mm'.
Info: Processing symbol 'NT4:NetTie:NetTie-2_SMD_Pad2.0mm'.
Info: Processing symbol 'Q1:Package_TO_SOT_THT:TO-220-3_Vertical'.
Info: Processing symbol 'R1:Resistor_SMD:R_0805_2012Metric_Pad1.20x1.40mm_HandSolder'.
Info: Processing symbol 'R2:Resistor_SMD:R_0805_2012Metric_Pad1.20x1.40mm_HandSolder'.
Info: Processing symbol 'R3:Resistor_SMD:R_0805_2012Metric_Pad1.20x1.40mm_HandSolder'.
Info: Processing symbol 'R4:Resistor_SMD:R_0805_2012Metric_Pad1.20x1.40mm_HandSolder'.
Info: Processing symbol 'R5:Resistor_SMD:R_0805_2012Metric_Pad1.20x1.40mm_HandSolder'.
Info: Processing symbol 'R6:Resistor_SMD:R_0805_2012Metric_Pad1.20x1.40mm_HandSolder'.
Info: Processing symbol 'R7:Resistor_SMD:R_0805_2012Metric_Pad1.20x1.40mm_HandSolder'.
Info: Processing symbol 'R8:Resistor_SMD:R_0805_2012Metric_Pad1.20x1.40mm_HandSolder'.
Info: Processing symbol 'R9:Resistor_SMD:R_0805_2012Metric_Pad1.20x1.40mm_HandSolder'.
Info: Processing symbol 'R10:Resistor_SMD:R_0805_2012Metric_Pad1.20x1.40mm_HandSolder'.
Info: Processing symbol 'R11:Resistor_SMD:R_0805_2012Metric_Pad1.20x1.40mm_HandSolder'.
Info: Processing symbol 'R12:Resistor_SMD:R_0805_2012Metric_Pad1.20x1.40mm_HandSolder'.
Info: Processing symbol 'R13:Resistor_SMD:R_0805_2012Metric_Pad1.20x1.40mm_HandSolder'.
Info: Processing symbol 'R14:Resistor_SMD:R_0805_2012Metric_Pad1.20x1.40mm_HandSolder'.
Info: Processing symbol 'R15:Resistor_SMD:R_0805_2012Metric_Pad1.20x1.40mm_HandSolder'.
Info: Processing symbol 'R16:Resistor_SMD:R_0805_2012Metric_Pad1.20x1.40mm_HandSolder'.
Info: Processing symbol 'R17:Resistor_SMD:R_0805_2012Metric_Pad1.20x1.40mm_HandSolder'.
Info: Processing symbol 'R18:Resistor_SMD:R_0805_2012Metric_Pad1.20x1.40mm_HandSolder'.
Change D8 value from LED_BUILTIN to Yellow.
Change D9 value from LED_BUILTIN to Yellow.
Change X2 value from 32.768kHz to ASEK-xxxMHz.
Change JP9 value from Reset GND to Reset Jumper.
Change J16 value from DC Motor PWR to MotorController_PWR_IP.
Change J22 value from Thermocouple to Thermocouple A.
Change J2 value from WS2821B LEDs to WS2821B Header.
Change J17 value from MotorController Output to MotorController.
Reconnect R17 pin 2 from 3V3_DC_MCU to 5V_DC_RPI.
Reconnect R19 pin 2 from 3V3_DC_MCU to 5V_DC_RPI.
Change JP10 value from RESET_gnd to Reset Jumper.
Reconnect J25 pin 5 from 3V3_DC_MCU to 5V_DC_RPI.
Reconnect R21 pin 2 from 3V3_DC_MCU to 5V_DC_RPI.
Change X1 value from 32.768KhZ to ASEK-xxxMHz.
Warning: No net found for symbol H2 pin 1.
Warning: No net found for symbol H2 pin 1.
Warning: No net found for symbol H2 pin 1.
Warning: No net found for symbol H2 pin 1.
Warning: No net found for symbol H2 pin 1.
Warning: No net found for symbol H2 pin 1.
Warning: No net found for symbol H3 pin 1.
Warning: No net found for symbol H3 pin 1.
Warning: No net found for symbol H3 pin 1.
Warning: No net found for symbol H3 pin 1.
Warning: No net found for symbol H3 pin 1.
Warning: No net found for symbol H3 pin 1.
Warning: No net found for symbol H3 pin 1.
Warning: No net found for symbol H3 pin 1.
Warning: No net found for symbol H4 pin 1.
Warning: No net found for symbol H4 pin 1.
Warning: No net found for symbol H4 pin 1.
Warning: No net found for symbol H4 pin 1.
Warning: No net found for symbol H4 pin 1.
Warning: No net found for symbol H4 pin 1.
Warning: No net found for symbol H1 pin 1.
Warning: No net found for symbol H4 pin 1.
Warning: No net found for symbol H4 pin 1.
Warning: No net found for symbol H5 pin 1.
Warning: No net found for symbol H5 pin 1.
Warning: No net found for symbol H5 pin 1.
Warning: No net found for symbol H5 pin 1.
Warning: No net found for symbol H5 pin 1.
Warning: No net found for symbol H5 pin 1.
Warning: No net found for symbol H5 pin 1.
Warning: No net found for symbol H5 pin 1.
Warning: No net found for symbol H5 pin 1.
Warning: No net found for symbol H6 pin 1.
Warning: No net found for symbol H6 pin 1.
Warning: No net found for symbol H6 pin 1.
Warning: No net found for symbol H6 pin 1.
Warning: No net found for symbol H3 pin 1.
Warning: No net found for symbol H1 pin 1.
Warning: No net found for symbol H6 pin 1.
Warning: No net found for symbol H6 pin 1.
Warning: No net found for symbol H1 pin 1.
Warning: No net found for symbol H1 pin 1.
Warning: No net found for symbol H1 pin 1.
Warning: No net found for symbol H1 pin 1.
Warning: No net found for symbol H1 pin 1.
Warning: No net found for symbol H4 pin 1.
Warning: No net found for symbol H6 pin 1.
Warning: No net found for symbol H1 pin 1.
Warning: No net found for symbol H1 pin 1.
Warning: No net found for symbol H2 pin 1.
Warning: No net found for symbol H2 pin 1.
Warning: No net found for symbol H2 pin 1.
Warning: No net found for symbol H6 pin 1.
Warning: No net found for symbol H6 pin 1.

Info: Total warnings: 0, errors: 0.

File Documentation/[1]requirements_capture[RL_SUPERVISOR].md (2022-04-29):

# [1]   Requirements Capture Form - [RL_SUPERVISOR]

_This form is intended to assist in capturing the requirements for new Open Source Embedded Systems Projects, <br>
its scope & implementation can be adapted to suit projects of varying complexity._

***************************************************************************************************************************************************************
## [1.1]Project Brief
_The project brief should contain an outline of the proposed project, with enough detail to derive a comprehensive list of requirements. The format, layout and
information provided can be tailored to project complexity_

### Project Brief - [RL_SUPERVISOR]

Design a PCB to provide power to remote labs experiments, which involve students programming microcontrollers remotely.
PCB should also provide a supervisory role, blocking actuation of experimental hardware if it is likely to cause damage to the equipment.

This allows students to upload their own code to a bare bones microcontroller, without risk of causing hardware damage or unsafe conditions.

###### Further Reading
[Tim Drysdale - Safety Circuit](https://github.com/timdrysdale/safetycircuit)

#### Current State

~70 remote labs experiments, each requiring:
- 12v supply for motors
- 12v supply for LED lighting
- 5v supply for Raspberry Pi
- 5v supply for Microcontrollers
- 5v supply for 5 port switch

Power Provisions:

12vDC 240W PSU, daisy chained power to 4 x Experiment Boxes

Comms:

5 Port switch in one box, ethernet comms from each box in the stack of 5 meet there for connection to LAN

##### Current PCB

Using Arduino Nano 33 IoT

https://content.arduino.cc/assets/NANO33IoTV2.0_sch.pdf

Existing Spinner PCB V1? or V0?
https://github.com/practable/spinner-nidec/blob/main/hw/pcb/PCB_PIDController.png

#TODO:
_Find Repo or KiCad files for Existing motor drive board_

#### Experiment Description

##### Spinner

- 	DC Motor & Controller
- 	Optical Encoder
- 	Temperature Sensor

Encoder needs calibration on power up.

##### Digger

As ***Spinner*** Plus:

-	Servo - CS238MG (4.8 - 6.0v)
- 	Limit switches? Probably not

Encoder calibrated then used to limit movement of DC motor.
Servo position limited to avoid collision.

Servo blocked from actuation while digger is moving, and vice versa.

##### Govenor

As ***Spinner*** Plus:

- Stepper Motor
- 2x limit switches (1 definite, 1 potential) - OR gate for virtual/spoof limit switch

Limit switches limit movement of stepper motor.

Stepper motor blocked from actuation while govenor is in motion and vice versa.

##### Pendulum

5v Electromagnet with 4 possible states:

-	Open Circuit
-	Closed Circuit - direct short via transistor BC547 & flyback diode
	- #TODO Research: dual transitor pass gate. - Simulate?
-	Energised (Positive Direction)
- 	Energised (Negative Direction)

-	600ppr Optical Encoder

-	Temperature sensor?

### Features & Functions of the New System

#### Supervisor MCU Requirements
Concept:
_Supervisor MCU manages system, performs its own calibrations to track experiment status and monitor for actions that could damage the apparatus_

[X]	-	SAMD21 MCU IC
[X]	- 	Encoder Calibration 
		- devolved requirement: Must control motor actuation during this process.
[X]	- 	Logic to prevent both Supervisor and Student Controllers from actuating hardware at the same time.
[X]	-	Depower motors & other actuators and alert user if temperature is approaching max: (90degC)?
[X]	-	Track & Report encoder Position & velocity independent of STUDENT MCU.
[X]	-	Cut power to DC motor in case of out of bounds operation for experiments that require this function.
[X]	-	Set boundaries of operation for Servo motor. Cut power/control if limits breached.
[X]	- 	Set hard limits of operation for stepper motor using limit switches. Alert the user & cut stepper motor if switches are actuated.
[X]	-	Prevent actuation of the servo while the rotating platform is in motion. Prevent platform rotation if servo is in motion.
[X]	- 	Prevent actuation of stepper motors if govenor is in motion. Prevent govenor rotation if stepper motor is in motion.
[X]	-	Note: in any case where power is cut to hardware, supervisor MCU must be capable of resetting the experimental apparatus to a stable "home" position and return control to the student MCU.
[X]	- 	Virtual Limit switches for students

##### Student MCU Requirements
Concept:
_Bare metal programming experience - The student should have full control of the MCU, the supervisor MCU is responsible for protecting the rest of the experimental apparatus from damage._

[X] -	SAMD21 MCU IC
- 	

- Control all experimental hardware i.e:
[X]	-	DC Motor Via Motor Controller
[x]	- Servo Via PWM output
[x]	- Stepper motor via Stepper Motor Controller.
[x]	- Electromagnetic actuator.
[x]	- Temperature Sensor?

##### Servo Control

- 	Detect PWM from Student PCB? 
-	Frequency Counter?
-	Seperate controller for high frequency signal aquisition.?
-	Op amp filtering into comparator ? - probably not , temperature issues, tuning, calibration.

#### Example Logic

#### Power Supply Requirements

#### Sub-Systems Specifications
##### Power Requirements Per Experiment
_Specific requirements for subsystems can be documented at this stage_    <br>
> a. steady power usage of 20W 1.7A at 12V (Maxxon AMax 32 236668 Graphite brushes, 20 Watt)[Estimated value, may change in future iterations] <br>
> b. peak power usage of 69W 5.7A at 12V (when motor stalled)  [Estimated value, may change in future iterations] <br>
> c. 5V power for the Raspberry pis, typically 1A per Raspberry Pi but Max 2.5A.

##### Interface Requirements

#### General Specifications/Requirements
_These specifications are going to be valid for most projects developed using this framework_
> 4. Circuit should be protected from reverse supply voltages. <br>
> 5. Circuit should be fuse protected <br>

#### Optional Features
_Any features or functions that are optional should be stated here_  <br>
>  1. Report Status & current usage for sustainabilty and maintainance purposes.  #NOTE: do we want to include this feature?
>  3. Use only connection types that can be operated with one hand. i.e. avoid screw terminals.

#### Design Optimisation
_What parameters of the design should be minimised/maximised?_

#### Design Tradeoffs
_Space for discussion and weighing up of features that may or may not be required_ <br>

### Modular System Potential

##### DC Motor Controller

- COTS
- Integrated

##### Stepper Motor Controller

- COTS
- Integrated

##### Pendulum Electromagnet

- Motor Controller?
- Integrated driver
- Daughterboard replacement

IF integrated:
On main PCB or Daughterboard?

Could 1 PCB be reconfigured for each experiment using daughterboards?

#### Motor Controller Options

Infineon DC Motor Sheild
https://uk.rs-online.com/web/p/shields-for-arduino/9062874?

L298N Dual Full Bridge Driver
https://docs.rs-online.com/6243/0900766b80060c26.pdf

Can drive stepper motors & DC Motors.

######## Current Guvnor Experiement PCB

DC Motor:
[Pmod HB3: H-bridge Driver with Feedback Inputs](https://digilent.com/shop/pmod-hb3-h-bridge-driver-with-feedback-inputs/)

Stepper Motor:
[DRV8825 Module](https://printermods.co.uk/products/sku10919)

### Supervisor Controller Circuit Topology

#### Problem

System must allow clear differentiation between STUDENT mcu involved in running experiment, and SUPERVISOR MCU which manages the system and supervises the STUDENT MCU, while programming remotely.

###### Option A

Student & Supervisor MCU both have dedicated CH340 USB interface. Select CH340 with programmable PID identifier to allow Raspi software to roboustly identify the STUDENT and SUPERVISOR MCUs using PIDs.
	Disadvantages:
	- Sourcing correct5 CH340 USB interface chip

##### Option B

STUDENT MCU has no direction USB interface, is programmed from SUPERVISOR MCU.
	Disadvantages:
	- Increase complexity of firmware requirements for Supervisor

##### Option C

SUPERVISOR MCU is programmed via UART from the raspberry pi - tested and proven on bench
STUDENT MCU is programmed via CH340 interface and USB, maintaining a familiure interface for students who may be interacting with the microcontroller

##### Option D

Both MCUs are programmed via USB, but supervisor MCU has a handshake procedure that responds to a specific data packet to "prove" it is the supervisor MCU

# DECISIONS THAT NEED TO BE MADE

- Stepper motor voltage - check specifications. Check current drivers.
- Servo PWM monitoring?

# DECISIONS THAT have been MADE

- 5v Power Supply - lM2589 Modules 2.5A max?
- Independent 12v to 5v PSU for servos.
- DC Motor - 12v - Infineon board

- MCU CH340 for Student
- Supervisor programmed directly from UART. 

- ISPs & UART For supervisor
- ISP & CH340 for student

#### Quality Assurance 
_What quality assurances or requirements, if any, need to be established?_

#### Notes
_Any Extra Notes?_

Software Reqirements: 

#### Concept
_Outline any concept or topology that may be worth exploring._

System Concept:

##### Power Distribution:

### Existing Products & COTS (Consumer Off The Shelf)
_The project brief may also contain information on currently available similar products and a brief description of the features they lack and a 
quick review of whether they can fullfill the aims of the project._

_______________________________________________________________________________________________________________________________________________________
## [1.2]High Level Requirements Description

*This section should contain a numbered list of all the specific high level requirements that can be gathered from the project brief, or from the client directly. <br>
High Level Requirements capture the intent and function of a system, without going into specifics of how these will be achieved or any specific implementations. I.E. They take a Black Box approach*

#### High Level Requirements should address:
> - Client Needs
> - Features & Functionality
> - Interfaces
> - Performance
> - Quality Attributes
> - Design Constraints
> - Regulations
> - Safety & Security
> - System

#### Requirements should be:
> - Specific           - Document a single feature or function requirement at a time.                                                 <br>
> - Quantifyable       - Provide quantifyable parameters, boundary limits of operation and/or design tolerences, rather than open ended specifications where possible.<br>
> - Self Contained     - Do not rely on assumptions to deliver information, as different engineers will make different assumptions, which may cause conflicts.
> - Traceable          - Assign each requirement an ID number, this will be used to trace any design decisions through the development process. <br>

_Good requirements are the foundation for successful development of a project, as it allows design decisions to be traced through the development process.
it also provides the information required to undertake successful **Verification** & **Validation**[^V&V]._ 

_______________________________________________________________________________________________________________________________________________________
## [1.3]Requirements Capture - [RL_SUPERVISOR]

| ID	| Sub-System 		| Requirement/Function 								| Notes												|
|---	|---				|---												|---												|
| R.1	| Supervisor MCU	| SAMD21											|													|
| R.2	| Supervisor MCU	| Encoder Calibration								|													|
| R.3	| Supervisor MCU	| Tracking Of Encoder position throughout experiment|													|
| R.4	| Supervisor MCU	| Prevent overheating of experimental apparatus 	|													|
| R.5	| Supervisor MCU	| Enable/Disable stepper motor function 			| TODO: Does it also need control of stepper motor? - Yes in order to reset it |	
| R.6	| Supervisor MCU	| Enable/Disable Servo actuation 					| TODO: Does it also need control of servo at all?	- Yes in order to reset it |	
| R.7	| Supervisor MCU	| Enable/Disable DC Motor control for Student & Supervisor	| Ensure that only 1 MCU is in control of actuators at any point in time	|
| R.8	| Supervisor MCU	| Provide soft or Virtual limits on DC motor movement		|											|
| R.9	| Supervisor MCU	| Provide soft or Virtual limits on Servo actuation to prevent out of bounds operation		|			|
| R.10	| Supervisor MCU	| Provide soft or Virtual limits on stepper motor actuation to prevent out of bounds operation			|	
| R.11	| Supervisor MCU	| Provide hard limits on stepper motor actuation to prevent out of bounds operation using limitswitches		|			|
| R.12	| Supervisor MCU	| Provide hard limits on stepper motor actuation to prevent out of bounds operation using limitswitches		|			|
| R.13	| Supervisor MCU	| Block actuation of Servo/Stepper if DC motor is moving & vice versa |	Priority given to the first thing moving? OR Priority given to DC Motor?|
| R.14	| Supervisor MCU	| Reset experiment to neutral condition in the case limits are breached |								|
| R.15	| Supervisor MCU	| Track Motor Driver PCB Temperature via over temp output|	  Check - Current Output or Fault Output?!												|	

|---	|---				|--- 												|---												|
| R.15	| Student MCU		| SAMD21											|													|
| R.16	| Student MCU		| Control over experimental hardware inc; DC Motor, Stepper Motor, Servo & Electromagnetic Actuator	|	|
| R.17	| Student MCU		| Direct access of encoder feedback data			|													|
| R.18	| Student MCU		| Direct or Virtual access of temperature sensor	|													|
| R.19	| Student MCU		| Virtual access of Limit switch data (spoofed from Supervisor MCU)	|									|
| R.20	| Student MCU		| Bare Bones Programming Experience  				|		Can this be quanfied in some way?			|

|---	|---				|--- 												|---												|
| R.21	| Power Supply		| 5v Power @ 0.5A max for MCUs						|													|
| R.22	| Power Supply		| 5v Power @ 2.5A max for Raspberry Pi				|													|
| R.23	| Power Supply		| 5v Power @ 2.5A max for Servo						|													|
| R.24	| Power Supply		| 12v Power Distribution for DC Motor Driver		|													|
| R.25	| Power Supply		| 12v Power Distribution for Stepper Motor Driver	|													|

|---	|---				|--- 												|---												|
| R.21	| Sensors			| Temperature Sensor to track motor temperature		|	Thermocouple or Digital Sensor?		https://www.mouser.co.uk/datasheet/2/609/ad8494_8495_8496_8497-1502317.pdf										|
| R.22	| Sensors			| Limit Switch Inputs (x2 definatly) (2x spare/Future Use?)		|													|
| R.23	| Sensors			| Optical Encoder - Distributed via buffers to both MCU	|													|

|---	|---				|--- 												|---												|
| R.21	| DC Motor			| 2A Protection fuse on power supply to motor sheild|													|
| R.22	| Sensors			| Limit Switch Inputs (x2 definatly) (2x spare/Future Use?)		|													|
| R.23	| Sensors			| Optical Encoder - Distributed via buffers to both MCU	|													|

#TODO  15/04/2022 Talk to Tim To Resolve Questions

1. Define relationship between servo and MCU control - how is that going to be tracked?
- Position does not need to be tracked but DOES need to be limited
- PWM from student to supervisor. analogRead and entroplate to safe servo positions     [x]

2. Clock Speeds? 48MHz?                                     
2a.	External Oscillator/ Internal Oscillator.
- External Oscillator     

See: https://blog.thea.codes/understanding-the-sam-d21-clocks/

See Page 1084: https://ww1.microchip.com/downloads/en/DeviceDoc/SAM_D21_DA1_Family_DataSheet_DS40001882F.pdf

See Problems with implementing external oscillators: https://forum.arduino.cc/t/custom-samd-board-external-crystal-problem/659008

"The datasheet for the SAMD21 Family states crystal load capacitance MAX for 32kHz oscillator is 12.5pF. So, you should try lower values." - Klaus_K Arduino Forums (2020)

Specify  9pF - 12.5pF for oscillator capacitors [x]

External oscillator requires 32.768 kHz Xtal     For running USB in host mode

Xtal might not be 100% required for our use, so specify on board is best but workable if unpopulated.   
Possible source? 
https://www.digikey.co.uk/en/products/detail/suntsu-electronics,-inc./SXO32C3B161-32.768K/14616211
[x]

### MCU Options
1. Pick MCU
AtMega328p
SAMD21 <- Advantages outweigh negatives of lesser understood hardware    [x]
3. crypto chip / wireless comms - required for bare bones SAMD21 if not using Nano IoT   < Not needed [x]
4. R.E. Identifying correct microcontroller, SAMD21 -- Device can be identified via unique 128bit serial code saved in registers  [x]

5.
PURPOSE OF (as shown on previous PCB):
Connection to grey 3D printed lighting strip from microcontroller NeoPixels?! - Both MCUs to be able to control [x]

STEPPER MOTOR DRIVER
https://protosupplies.com/product/drv8825-high-current-stepper-motor-driver/

~{SLP}    - Always Pull High no need for sleep mode  [x]
~{EN}   	- open circuit is pulled HIGH to enable, pull LOW to DISABLE    -- Needs to be both MCU  [x]
~{RST} - for stepper board and needs to be able to be actuated  - Maybe just supervisor but would be good to have both  

~{FLT} FAULT - LOW WHEN FAULT DETECTED - good to have

6.
Not Enough Pins on Nano 33 IoT unless other functions ristricted, I.E

- Does Stepper Motor Controller need sleep & reset, or can these be tied to GND/Vcc As required?
- Does Stepper Motor Controller need Mode functions, or can it be perminantly set to a specific mode - (dipswitches?)

- Stepper Motor Fault output - is this the overtemp output previously mentioned? - Supervisor control NO student control. - DIPSWITCHES if  out of pins
[x]

6.1.
https://docs.rs-online.com/91cb/0900766b81490d99.pdf
- DC Motor Controller - Current sense outputs -

 ~<470r (1%) Shunt resistor - to calculate current output from IS_1 and IS_2 see datasheet https://docs.rs-online.com/6a9d/0900766b81478095.pdf [x]

- DC Motor Driver board Inhibit pins - Does student need control of these or can supervisor just set them high when student is in control? YES
Single PWM fed to both PWM input on driver board
Inhibit pins are fed from student through supervisor - state machine 4 states, off(00), INH1(10), INH2(01), and FAULT (11) [x]

8.
PROGRAMMING BARE BONES BOARD. slight confusion...can it be done easily/directly over UART or are additional pins / hardware required. Should this be on board or off board
Yes UART works direct for dev board & raw MCU [x]

10.

Find the Name of International Finance office personell - get email or phone & talk directly to them.

Search personell directory for International and Finance.
Search linkedin

- Emotional blackmail focus on need for interns

11.

Shift Registers.
[x]
ry and make shift register relate to single task. 

max PWM speed is clock/number of bits - check suiotability for task before commiting. - No need not put any PWM channels through shift register. [x]

#TODO 21/04/2022

More Questions to Ask

1. Rotary Encoder Index pin? - Test to see what is required  - Index doesnt seems to be required - leaving connected anyway [x]

2. Limit Switches - quantity of inputs, 3 seems high - Solution Only have 1 or 2 max on IoT board, keep the other as an option for the raw MCU option [x]

4. Applying PWm to both pins and using INH pins does NOT seem to work Belive this is due to full H-Bridge topology - both sides must be active to pass current
 - Both INH inputs MUST be HIGH and PWM is applied to 1 of IN1 or IN2  [x]
 
 BUT we can make it function like this using 2 AND gates. 

Logic to block simaltanious HIGH ? - This can be handled by supervisor.  [x] Implemented

5. at the moment, each subsystem is enabled/disabled by supervisor individually, should there just be 1 master enable/disable to save pins?
 - eather way I think shift register will be needed. - Solved [x]

7.  Shift Register: http://ediy.com.my/blog/item/114-using-hef4094-shift-registers-with-arduino 4094
https://www.ti.com/lit/ds/symlink/cd74hc4094.pdf

Example sketch written for shift registers, making them as easy to access as arduino digital pins. given descriptive names eg D14 - D22 [x] Done

#TODO 25/04/2022

1. All output pins from Nano IoT Mirrored to Raw MCUs [x]

2. Test Optical Encoder. [x]  Done - working Index pin does not seem required but left wired incase future use

3. Check logic gates usage - make sure packages assigned correctly [x] - also checked all ICs and multi package parts

4 Xtal [x]

3. Purpose of Line receiver - datasheet for some encoder devices specify this - hmm maybe still an issue, could use additional buffers - Moved to later todo
6. Line driver for optical encoder.   - Dont think is nessissary but Clarify [x]

7. Got rid of Limit Switch 3 to give option to have all shiftregister pins go to IO pins instead [x]

8. Hook Up final lines from student to logic map - Stepper reset? [x]

9. Prog Header for Student - also look at USB natve - Done both [x]

10 Student Xtals [x]

11 Super Xtals [x]

12 check thermo driver for specifications [x]

13. Final decision on student servo PWM thhrough supervisor? [x]

14. Check shift register outputs the same across both MCUs [x]

15 V_USB Usage? - put it on a jumper [x]

17. Test Points

18. Check logic gate for IC's available [x]

# FINAL CHECKS & Design Review

1. Line driver for optical encoder.   - Dont think is nessissary but Clarify [x]  - It essensially has a line driver through buffers

16. suitability of dropping 12v down to 3v3 ? Not liking - moved to Raspberry pi 5v  - need to check current draw on MCU, quieccent current on ICs?  [x]  - Before microcontroller was powered from raspberry pi USB so should not be a problem

2. ERC fail - EP Pin Not Connected on ATSAMD21G [x] - exposed pin I.E heatsink pin? I have tied to GND for heatsinking purposes

3. Resistor values for thermocouple - filter - Low Pass as we want the smoothed DC and get rid of the noise. I have assumed ~100Hz is a suitable cutoff, with 10k resistors corner frequency for the basic filter is ~159Hz,
however this is an abritrary value I have picked. I dont have any experience with smoothing sensor readings using analog filters. The actual circuit given in the application notes is more complex than a basic RC Filter- and I do not
know how to evaluate it more accuratly. [x] - Worst come the worst we can change the value of these resistors

4. When ROUTING - Ensure that NET LABELS do not connect across sheets - care taken to ONLY connect through sheets using HIARARCHICAL PINS. - Replace all global labels with NET LABELS? [x] - Still take care when routing to double check against schem

5. Test Points? 

 - Liase with Tim to make sure pin defintions are suitable for tasks, no unforseen errors with pin assignments.
 - Suitability of analog buffers - can be tested? [x] Tims seal of approval
 - suitability of digital buffers - [x] - See max signal speed considerations below.

 # TIMS Notes
 
 1. add 1k resistors in series to digital buffers to limit current  [x]

 Max frequency of OE
 
 motor 4000 rpm
  /60 = rpS
  
 *1000 transitions per revolution (500 pulses)
 
 33 kHz pulse train
 
 1/33k = period
 
 period = 30uS  BUT needs to transitioon bothwasy there max = 15uS
 
 / 4.6 (rise time to charge RC circuit)
 
 3uS max time constant 
 
 3uS = RC 
 
 20nS for 
 
 2. CLR between ANY student / supervisor I/O lines  limit current [x]

 3. Analog buffers add CLR to student output to avoid them driving high into output of opamp buffer. [x]

 4. DOUBLE CHECK USB POLARITY [x][x]

 5. add addition power header [x]

 # CHANGELOG 26/04/2022
 
 1. Moved 3v3 regulator from 12v bus to 5V RPI bus, to avoid the large V drop of 12 to 3v3 & save on a DC/DC Module - 3 felt excessive and RPI should be capable of also running microcontrollers and logic
  - Note can this be estimated?

# CHANGELOG 28/04/2021 
 2. Added Reset Buttons
 3. Change 10mH inductor for ferrite bead specified for Arduino Nano IoT 33

 Noticed TL074 Min voltage requirements are too high. Looking for more suitable op-amp with Vcc ~3V3 - Solved [x]

 Look at oscillator - maybe MEMs over Xtal

## Devolved Requirements
_Requirements that are established to meet higher level requirements_

| ID	| Sub-System 		| Requirement/Function 		| Devolved Requirement														| Hardware/Software Requirement	|
|---	|---				|---						|---																		|---							|
| DR.2.1| Supervisor MCU	| Encoder Calibration		| Prevent Student MCU from actuating motor while calibration is undertaken	| Both 							|
| DR.2.2| Supervisor MCU	| Encoder Calibration		| Enable supervisor MCU to actuate motor while calibration is undertaken  	|	 Both							|
| DR.3.1| Supervisor MCU	| Tracking Encoder			| Duplcation of digital encoder signals to feed both MCU's					|  Hardware						|
| R.3	| Supervisor MCU	| Encoder Calibration		| Hardwired logic to enable & disable control of motor. Buffers to duplicate digital signal from encoders|	Run calibration on startup or via remote API|

### Programming SAMD21

_Programming the Arduino Nano IoT33 via both USB and UART is now solved, however.. What about programming a bare bones SAMD21 if that is the route we decide to go down?_

 Links to various methods foubnd provided below: <br>
 
 https://arduino.stackexchange.com/questions/32116/barebones-arduino-zero-with-atsamd21g18
 https://www.avdweb.nl/arduino/samd21/sam-d21
 https://microchipdeveloper.com/atstart:sam-d21-bootloader

 https://ww1.microchip.com/downloads/en/DeviceDoc/SAM_D21_DA1_Family_DataSheet_DS40001882F.pdf

- 	Encoder Calibration 
	- devolved requirement: Must control motor actuation during this process.

- 	Logic to prevent both Supervisor and Student Controllers from actuating hardware at the same time.

-	Depower motors & other actuators and alert user if temperature is approaching max: (90degC)?

-	Track & Report encoder Position & velocity independent of STUDENT MCU.

-	Cut power to DC motor in case of out of bounds operation for experiments that require this function.

-	Set boundaries of operation for Servo motor. Cut power/control if limits breached.

- 	Set hard limits of operation for stepper motor using limit switches. Alert the user & cut stepper motor if switches are actuated.

-	Prevent actuation of the servo while the rotating platform is in motion. Prevent platform rotation if servo is in motion.

- 	Prevent actuation of stepper motors if govenor is in motion. Prevent govenor rotation if stepper motor is in motion.

-	Note: in any case where power is cut to hardware, supervisor MCU must be capable of resetting the experimental apparatus to a stable "home" position and return control to the student MCU.

- 	Virtual Limit switches for students

When to review? <br>
*High level requirements should undertake a review process,* ***Validation***, *to ensure they meet the clients needs, before any further development takes place.*<br> 

<!--After review, please see the next document in the design process* [[2]Low Level Requirements Capture](https://github.com/PanGalacticTech/project_template/blob/main/%5B2%5DLL_requirements_capture.md) -->

_______________________________________________________________________________________________________________________________________________________

[^V&V]: Verification & Validation - What is it? <br>
        - Verification - _"Does the implementation meet the requirements?"_ <br>
        - Validation   - _"Are the requirements correct"_
        
[^2]: Assumption made that only 1 motor will be in stall condition, with others running typically.

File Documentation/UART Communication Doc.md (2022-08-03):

# UART Communication with Arduino Nano 33 IoT and Odroid C4 (Ubuntu MATE)/Raspberry Pi (Raspberry OS)
*Author: Bhavith Manapoty
Created On: 28 July 2022
https://bhavithmanapoty.com*

**Note: All steps are identical for ODROID and Pi unless otherwise stated.**

**For ODROID, the home directory is /home/odroid
For Pi, the home directory is /home/pi**

**This documentation has been tested for both ODROID and Pi, but all comands in this documentation were initially written for ODROID. Thus, all file location commands might need to be modified to match your device appropriately.**

### Connections:
|Nano|RPi/ODROID Pin No.|RPi Pin Name|ODROID Pin Name|
|-----|-----------|--------------|-------------------|
|3v3|1|3v3|3v3|
|GND|6|GND|GND|
|Rx0|8|Tx|Tx|
|Tx0|10|Rx|Rx|
|RST|12|GPIO 18|GPIO 1|

## Install Arduino-CLI

```
sudo apt-get update && upgrade -y
```
```
curl -fsSL https://raw.githubusercontent.com/arduino/arduino-cli/master/install.sh | sh
```
```
arduino-cli
```
The above command should output a list of all available arduino commands. If you get an error that says arduino-cli cannot be found, then you might need to add it to your PATH, by doing the following.
```
nano ~/.bashrc
```
Next add the following line to the end of the file.
```
export PATH=$PATH:/home/pi/bin
```
Now we need to reboot our device.
```
sudo reboot
```
## Configure Arduino-CLI:
Once the installation script has completed we will first need to create a configuration file using the following command.
```
arduino-cli config init
```
This will create a configuration YAML file and echo the path in which the file was created.

## Create Blink Sketch
Now we need to create our first sketch to upload. There is some further configuration required so for now we will just create a basic blink sketch in order to complete the configuration.

```
arduino-cli sketch new blink
```
```
nano blink/blink.ino
```
In this file, we need to add the following code:
```
void setup() {
    pinMode(13, OUTPUT);
}
 
void loop() {
    digitalWrite(13, HIGH);
    delay(1000);
    digitalWrite(13, LOW);
    delay(1000);
}
```

## Modify Arduino-CLI to enable Serial UART
Now, we need to add the board cores for the Arduino AVR Boards and SAMD boards. To this, run the following commands:
```
arduino-cli core update-index
```
```
arduino-cli core install arduino:avr
```
```
arduino-cli core install arduino:samd
```
```
arduino-cli core update-index
```

Now we can make the necessary modification to arduino-cli in order to support the GPIO serial port. The serial port itself will work without modification, however we need to add DTR functionality so that the Arduino is reset into bootloader mode by a spare Raspberry Pi GPIO pin. For this, we need to locate the avrdude folder. This folder location can change for every installation and thus needs to be found using a verbose output from arduino-cli.

Run the following command:
```
arduino-cli compile --fqbn arduino:avr:nano blink -v
```

The compiler will run with more output than usual, producing a mess of output before echoing the usual success message. Within this information you will be able to see the path to the tools folder towards the end of the output.

For me, the path is ```cd /home/odroid/.arduino15/packages/arduino/tools/```. Once in this directory, we need to open the bin directory.
```
cd avrdude/6.3.0-arduino17/bin
```
Next we need to rename the avrdude file within the bin directory to avrdude-original.
```
mv avrdude avrdude-original
```
Now we can download the modified avrdude files by entering the following curl commands.
```
curl https://raw.githubusercontent.com/Siytek/avrdude-rpi/master/autoreset -o autoreset
```
```
curl https://raw.githubusercontent.com/Siytek/avrdude-rpi/master/avrdude -o avrdude
```
Finally we need to install some dependencies to support the autoreset script, so go ahead and run the following command.
```
sudo apt-get install -y python-dev python-rpi.gpio minicom
```

**NOTE: To try and replicate the double tap reset required for Nano IoT33, we need to modify the new autoreset avrdude python file**
```
nano /home/odroid/.arduino15/packages/arduino/tools/avrdude/6.3.0-arduino17/bin/autoreset
```
added these lines to the bottom of ```def reset()```
```
#added lines guessing at required delays
  time.sleep(0.5)
  GPIO.output(pin, GPIO.HIGH)
  time.sleep(0.32)
  GPIO.output(pin, GPIO.LOW)
  time.sleep(1)
```
### Instructions for ODROID C4:
If you are using an ODROID C4, we also need to change the pin Number in the autoreset file. If you are using a Raspberry Pi, skip to the next section.

Run the following command
```
nano /home/odroid/.arduino15/packages/arduino/tools/avrdude/6.3.0-arduino17/bin/autoreset
```
and change the following line
```pin=18``` to ```pin=1```

This changes the GPIO Pin Number that is used by the script. ODROID uses GPIO Pin 1 wheras Raspberry Pi uses GPIO Pin 18.

-------------------------------------------
We also need to modify user permissions to make each file executable by any user.
```
sudo chmod ugo+rwx avrdude
sudo chmod ugo+rwx avrdude-original
sudo chmod ugo+rwx autoreset
```
Finally, we need to add the ```bin``` folder to our PATH
Navigate to the directory to be added to PATH
``` cd /home/pi/.arduino15/packages/arduino/tools/avrdude/6.3.0-arduino17/bin```
and enter the following command.
```
PATH="$(pwd):$PATH"
```
This needs to be repeated every time the Pi/ODROID is rebooted. To avoid this, this can be added to the bash file. To do this, enter the following command
```
sudo nano ~/.bash_profile
```
and add the following line at the end of the file.
```
export PATH="$PATH:/home/pi/.arduino15/packages/arduino/tools/avrdude/6.3.0-arduino17/bin"
```
Then run the following command
```
source ~/.bash_profile
```
This will permanently update your PATH to include the required folder.

Now when arduino-cli calls for avrdude, the newly added bash script will launch the original avrdude with the addition of using the autoreset script to pulse the Arduino reset pin just at the correct time. Awesome!

## Programming the Arduino Nano 33 IoT
Make the necessary connections as shown in the table at the start of the page and run the following commands.

First, we need to compile our sketch.
```
arduino-cli compile --fqbn arduino:samd:nano_33_iot blink
```
Next, we need to check which Serial port is being used by our Arduino Board. To do this, run the following command.
```
arduino-cli board list
```
This will show the available boards and their port. If there are multiple ports being displayed, then it is just trial and error until you find the right one :)

For me, my board is connected to port /dev/ttyS1.
Once you have your port, we can upload the code to the Arduino.

We need to place the Arduino Nano 33 IoT in programming mode by double clicking the reset button. Then run the following command.
```
   arduino-cli upload --port /dev/ttyS1 --fqbn arduino:samd:nano_33_iot blink
```
This should successfully upload your code to the Arduino Nano 33 IoT through UART Communication from the Raspberry Pi or ODROID C4.

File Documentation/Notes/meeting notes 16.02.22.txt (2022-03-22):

2nd project

more modular

5v out
12v out
atmega328p
i2c bus out to raspberry pi

look for 8A buck converter

simplified

TODO:
1. PCB layout Finish. Extra Vout terminal 24v 12 & 5v. if space add an extra USB and DC output
	EMF Concerns? 
	Ground Plane on bottom
	Chunky tracks on top for power
	
2. buck conversion board simple PSU with I2c for generic experiments
3. microcontroller babysitter project for each experiment.

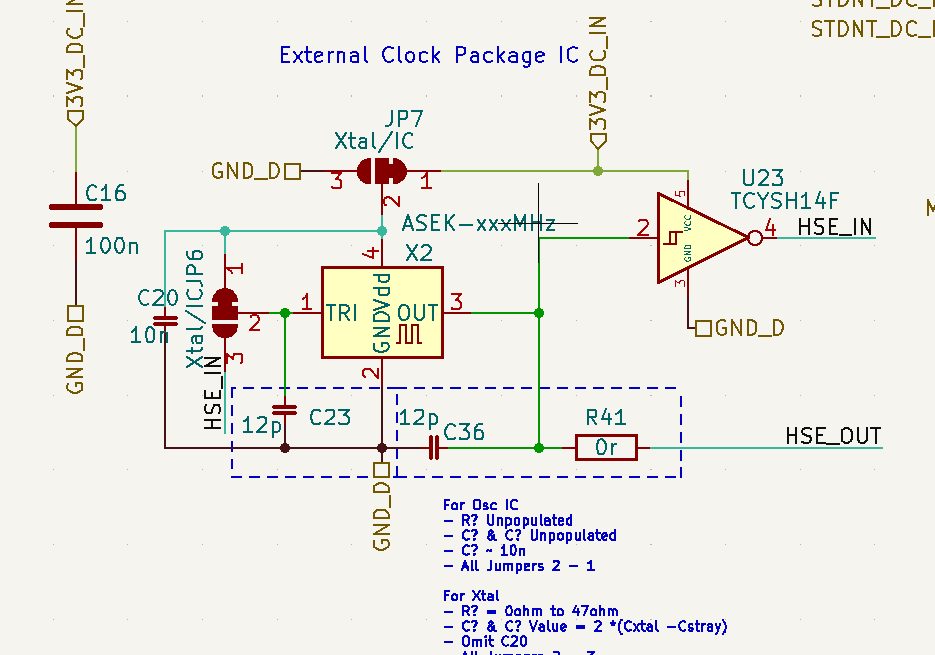
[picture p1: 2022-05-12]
Documentation/Media/Revised Clock Schematic.png

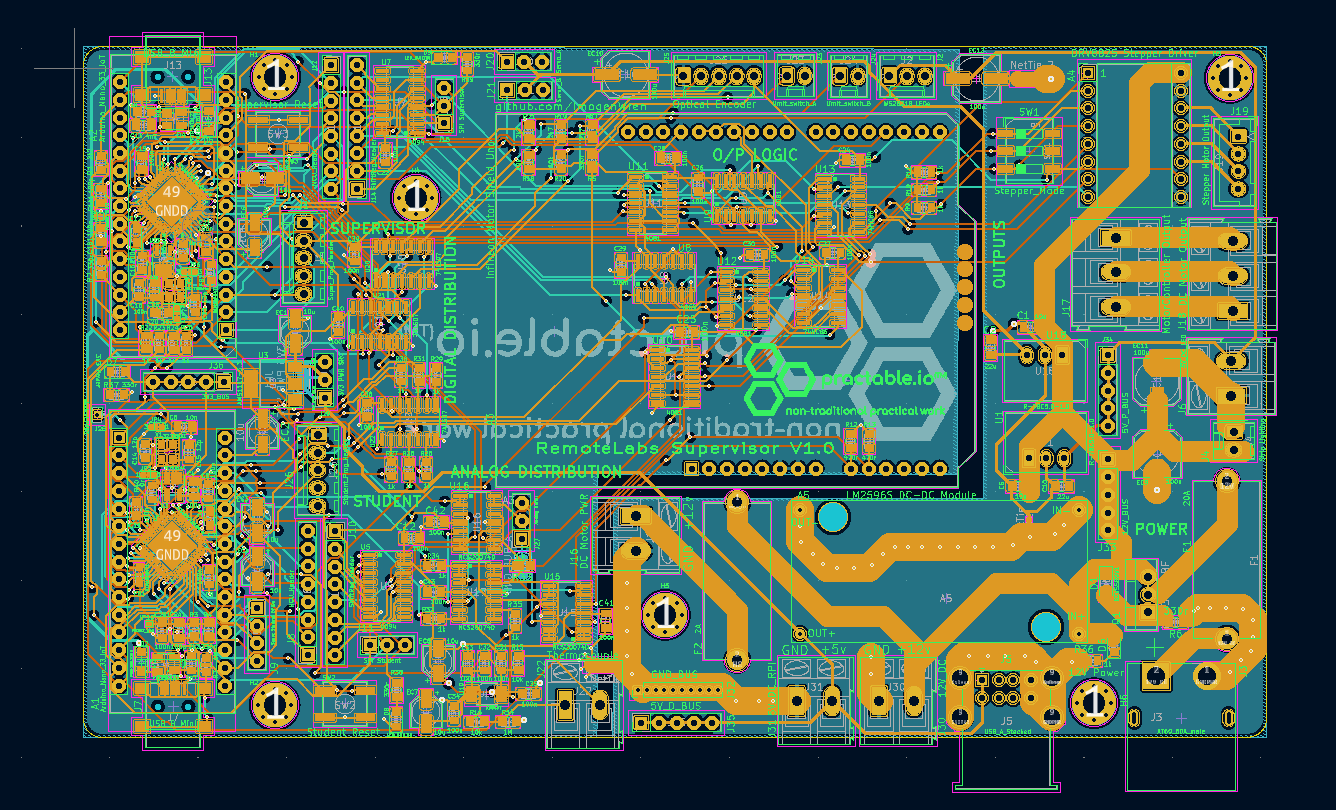
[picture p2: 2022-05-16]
Documentation/Media/RemoteLabsSupervisor V1.0 Renderings & CAD/RemoteLabs Supervisor PCBV1.0 CAD Design.png

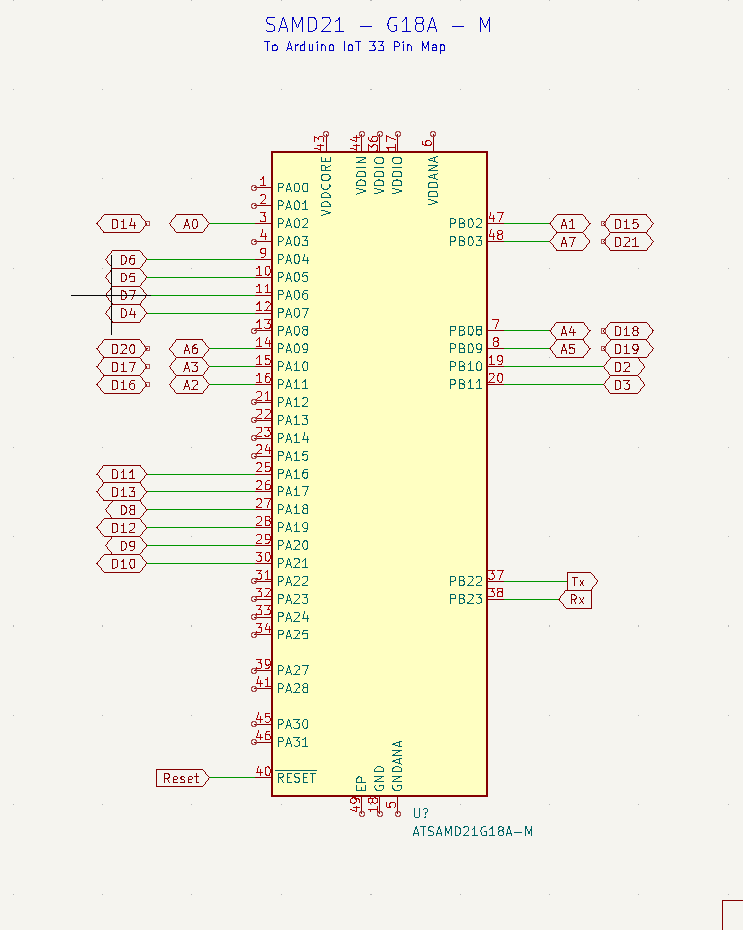
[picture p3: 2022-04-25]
Documentation/datasheets-reference-docs/SAMD21 Schematic Requirements/SMD21G to Arduino Nano IoT 33 pinmap.png

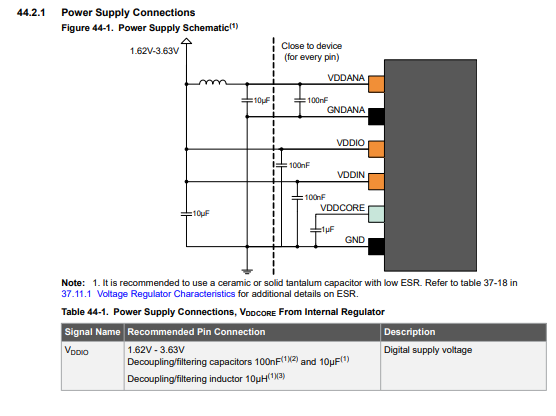
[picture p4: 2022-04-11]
Documentation/datasheets-reference-docs/SAMD21 Schematic Requirements/SAMS21.power_requirements.png

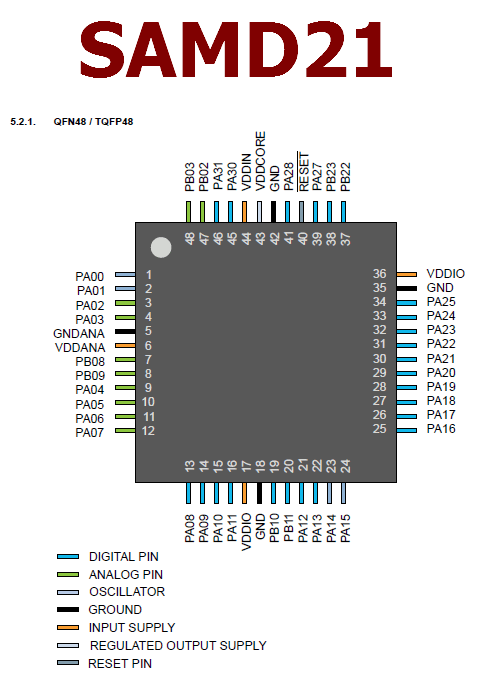
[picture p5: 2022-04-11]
Documentation/datasheets-reference-docs/SAMD21 Schematic Requirements/SAMD21-pinout-datasheet.gif

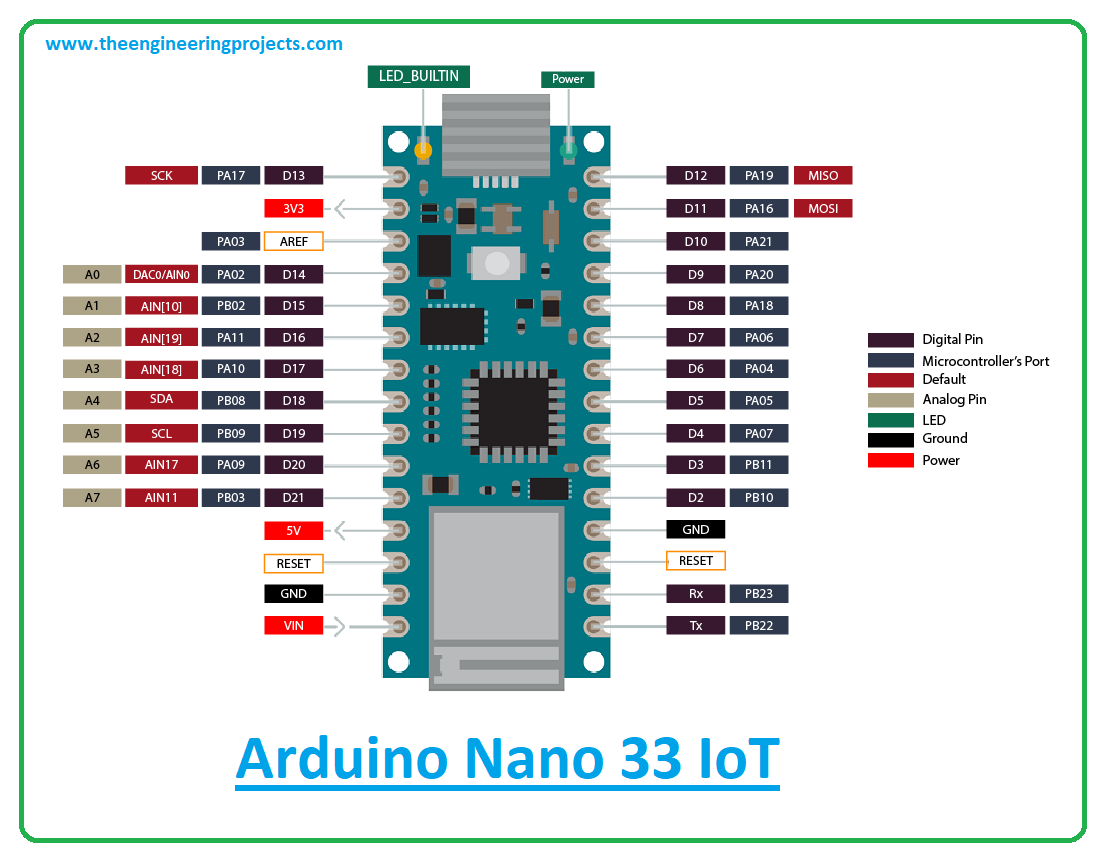
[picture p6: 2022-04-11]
Documentation/datasheets-reference-docs/SAMD21 Schematic Requirements/introduction-to-arduino-nano-33-iot.png

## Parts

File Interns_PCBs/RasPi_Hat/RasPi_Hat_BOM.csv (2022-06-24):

Id | Designator | Package | Quantity | Designation | Supplier and ref
1 | J2 | Molex_KK-254_AE-6410-05A_1x05_P2.54mm_Vertical | 1 | Arduino Serial
2 | J1 | Molex_KK-254_AE-6410-02A_1x02_P2.54mm_Vertical | 1 | Fan
3 | J3 | PinHeader_2x20_P2.54mm_Vertical | 1 | Pi Header

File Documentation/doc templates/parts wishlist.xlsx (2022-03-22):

Type | Value | Footprint | | Price(pU) | Min Quantity | Price(min Q) | JLC Part No | Vmax | SMD/TH | Manufacturer | MFG Part # | Basic Part? | Additional Cost | Notes
Film/MLCC | 100n | 0805 | 0.0046 | 20 | 0.092 | C49678 | 100 | SMD |  |  | Yes | 0
Film/MLCC | 22n | 0805 | 0.0112 | 20 | 0.224 | C1804 |  | SMD |  |  | Yes | 0
Electrolytic Capacitor | 100u | 6.3x7.7 | 0.0895 | 900 | 80.55 | C65221 |  | SMD |  |  |  | 3
Electrolytic Capacitor | 22u | 6.3x5.4 | 0.0383 | 10 | 0.383 | C72505 |  | SMD |  |  |  | 3
Film/MLCC | 1n | 0805 | 0.0076 | 20 | 0.152 | C46653 |  | SMD |  |  | Yes | 0
Electrolytic Capacitor | 680u | 12.5x20 | 0.2914 | 1 | 0.2914 | C270015 |  | PTH |  |  |  | 3
Electrolytic Capacitor | 220u | 6.3x7.7 | 0.0467 | 10 | 0.467 | C2887273 |  | SMD |  |  | Yes | 0
Film/MLCC | 4n7 | 0805 | 0.0054 | 20 | 0.108 | C1744 |  | SMD |  |  | Yes | 0
Zener Diode | 18v | MINIMELF | 0.0289 | 20 | 0.578 | C410854 |  | SMD |  |  |  | 3
LED | Blue | 0805 | 0.0380 | 20 | 0.76 | C138557 |  | SMD |  |  |  | 3
Schottky Diode 1N5821 | SS36-E3 | DO-214AB | 0.3063 | 2 | 0.6126 | C35722 | 60 | SMD |  |  | Yes | 0
PRTR5V0U2X |  | SOT-143 | 0.0649 | 10 | 0.649 | C2827688 |  | SMD |  |  |  | 3
LED | green | 0805 | 0.0178 | 20 | 0.356 | C84257 |  | SMD |  |  |  | 3
LED | red | 0805 | 0.0123 | 20 | 0.246 | C84256 |  | SMD |  |  | Yes | 0
USB Connector | A | USB-A-TH | 0.0343 | 20 | 0.686 | C46406 |  | TH |  |  |  | 3
USB Connector | Mini B | USB mini-B - Lumburg | 0.0615 | 10 | 0.615 | C2681563 |  | SMD | SHOU HAN | MINI 5PTP |  | 3
Inductor | 10uH | 0805 | 0.0166 | 20 | 0.332 | C1046 |  | SMD | Sunlord | SDFL2012S100KTF | Yes | 0
Inductor | 33uH | 12x12x8 | 0.3181 | 20 | 6.362 | C339951 |  | SMD | YJYCOIN | YPRH1207-330M |  | 3
Power MOSFET | IRF5305 | TO-263-2 | 1.1936 | 20 | 23.872 | C878890 | 55 | SMD | VBsemi Elec | IRF5305STR
MOSFET P-Channel | SI2319CDS-T1-GE3 | SOT23-3 | 0.1069 | 15 | 1.6035 | C558254 |  | SMD | VBsemi Elec | SI2319CDS-T1-GE3 |  | 3
NPN BJT | BC817 | SOT-23 | 0.0177 | 20 | 0.354 | C181151 | 50 | SMD | Guangdong Hottech | BC817-40 | Yes | 0
PNP BJT | BC807 | SOT-23 | 0.0271 | 20 | 0.542 | C8587 | 50 | SMD |  |  |  | 3
Resistors | 10k | 0805 | 0.0222 | 20 | 0.444 | C17414 |  | SMD | UNI-ROYAL(Uniroyal Elec) | 0805W8F1002T5E |  | 3
Resistors | 1k | 0805 | 0.0222 | 20 | 0.444 | C17513 |  | SMD |  |  |  | 3
Resistors | 330r | 0805 | 0.0222 | 20 | 0.444 | C17630 |  | SMD | UNI-ROYAL(Uniroyal Elec) | 0805W8F3300T5E | Yes | 0
Resistors | 560r | 0805 | 0.0032 | 20 | 0.064 | C28636 |  | SMD | UNI-ROYAL(Uniroyal Elec) | 0805W8F5600T5E | Yes | 0
Resistors | 470r | 0805 | 0.0028 | 20 | 0.056 | C114564 |  | SMD | YAGEO | RC0805FR-07470RL | no | 3
Resistors | 2k0 | 0805 | 0.0027 | 20 | 0.054 | C17604 |  | SMD | UNI-ROYAL(Uniroyal Elec) | 0805W8F2001T5E | yes | 0
Resistors | 2k2 | 0805 | 0.0026 | 20 | 0.052 | C17520 |  | SMD | UNI-ROYAL(Uniroyal Elec) | 0805W8F2201T5E | Yes | 0
Resistors | 1M | 0805 | 0.0025 | 20 | 0.05 | C17514 |  | SMD | UNI-ROYAL(Uniroyal Elec) | 0805W8F1004T5E | Yes | 0
Resistors | 220r | 0805 | 0.0025 | 20 | 0.05 | C17557 |  | SMD | UNI-ROYAL(Uniroyal Elec) | 0805W8F2200T5E | Yes | 0
Tactile Switch Pushbutton | SPST | EVQPE1 | 0.0544 | 10 | 0.544 | C455280 |  | SMD | XUNPU | TS-1088R-02026 |  | 3
ESP32-WROOM-32U |  | ESP32- | 4.0605 | 1 | 4.0605 | C328062 |  | SMD |  |  |  | 3
AMS1117-3.3 3V3 LDO | 3V3 | SOT-223-3_TabPin2 | 0.1734 | 2500 | 433.5 | C6186 |  | SMD |  |  | Yes | 0
AtMega328p-MU |  | QFN-32 | 8.9386 | 1 | 8.9386 | C967933 |  | SMD | Microchip Tech | ATMEGA328PB-MU |  | 3
ACS712xLCTR |  | SOIC-8_3.9x4.9x1.27 | 2.8912 | 1 | 2.8912 | C9932 |  | SMD | Allegro MicroSystems, LLC | ACS712ELCTR-30A-T |  | 3
LM2596S-5 | 5Vfixed | TO-263-5 | 0.7778 | 1 | 0.7778 | C347421 |  | SMD | UMW(Youtai Semiconductor Co., Ltd.) | LM2596S-5.0 |  | 3
CH340 |  | SOP/SOIC-16_3.9x10.1x1.27P | 0.8454 | 1 | 0.8454 | C84681 |  | SMD | WCH(Jiangsu Qin Heng) | CH340C |  | 3
TXS0102DTC |  | SSOP-82.8x3.0x0.65 | 0.5977 | 1 | 0.5977 | C324082 |  | SMD |  |  |  | 3
TL431 |  | SOT23-3 | 0.0394 | 15 | 0.591 | C181103 |  | SMD |  |  |  | 3
HEF4093 NAND Gate Shmitt trigger |  | SOIC-14_3.9x8.7x1.27 | 0.2356 | 1 | 0.2356 | C7867 |  | SMD | Nexperia | HEF4093BT,653 |  | 3
5032-4P Xtal | 16MHz | Xtal_SMD_abracon_ABM3C-4p_5.0x3.2 | 0.4071 | 1 | 0.4071 | C242216 |  | SMD |  |  |  | 3
MOSFET | SI2301CDS | SOT-23-3 | 0.0941 | 15 | 1.4115 | C10487 |  | SMD |  |  | Yes | 0
1.27mm Pin Headers - Male | 3 pin | HDR-TH_3P-P1.27-V | 0.0255 | 1 | 0.0255 | C24980 |  | PTH | BOOMELE(Boom Precision Elec) | C24980 |  | 3
AVR-6pin-ISR header | 2x3pin | HDR-TH_6P-P2.54-V-R2-C3-S2.54_A2541WV-2X3P | 0.1282 | 1 | 0.1282 | C225518 |  | PTH | CJT(Changjiang Connectors) | A2541WV-2x3P
Screw Terminal | 2 pin | CONN-TH_2P-P5.08_DB128L-5.08-2P | 0.15350 | 1 | 0.1535 | C395868 |  | PTH | DIBO | DB128L-5.08-2P-GN-S |  |  | 18A
1.27mm Pin Headers - Female | 10 pin | HDR-TH_10P-P1.27-V-M | 0.1714 | 1 | 0.1714 | C124392 |  | PTH | Ckmtw(Shenzhen Cankemeng) | B-2201S10P-A121
 |  |  |  | Total | 576.7725 |  |  |  |  |  | Additional Costs | 78

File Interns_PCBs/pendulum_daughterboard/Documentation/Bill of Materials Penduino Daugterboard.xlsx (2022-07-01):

Component Name | Component ID | quantity | Value | Description | Vendor | Part Number | Link | Unit Price (ex. VAT) | Requisition Number | Ordered | Q Boards | Total Price
logic IC AND Gate | IC1 | 1 | NA |  | Farnell | MC74HC08ADG | https://uk.farnell.com/on-semiconductor/mc74hc08adg/ic-74hc-cmos-smd-74hc08-soic14/dp/9666907 | 9666907 | 0.63 | 32563 | Yes | 45 | 28.35
Logic IC OR Gate | IC4 | 1 | NA |  | Farnell | MC74HC32ADG | https://uk.farnell.com/on-semiconductor/mc74hc32adg/ic-74hc-cmos-smd-74hc32-soic14/dp/9666966?st=2%20input%20or%20gate | 9666966 | 0.57 | 32563 | Yes | 44 | 25.08
Logic IC NAND Gate | IC3, IC2 | 2 | NA |  | Farnell | MC74ACT00DG | https://uk.farnell.com/on-semiconductor/mc74act00dg/ic-quad-nand-gate-2i-p-soic-14/dp/1652018?st=2%20input%20nand%20gate | 1652018 | 0.68 | 32563 | Yes | 43 | 58.48
LED Green | D1 | 1 | NA | Green LED | Farnell | MP008291 | https://uk.farnell.com/multicomp-pro/mp008291/led-green-70mcd-576nm-0805/dp/3796323?st=0805%20smd%20led | 3796323 | 0.11 | 32563 | Yes | 45 | 4.95
LED Orange | D2 | 1 | NA | Orange LED | Farnell | KPT-2012SECK | https://uk.farnell.com/kingbright/kpt-2012seck/led-orange-0805-smd/dp/2099237 | 2099237 | 0.12 | 32563 | Yes | 45 | 5.4
LED Red | D3 | 1 | NA | Red LED | Farnell | MP008293 | https://uk.farnell.com/multicomp-pro/mp008293/led-red-220mcd-626nm-0805/dp/3796325 | 3796325 | 0.1 | 32563 | Yes | 45 | 4.5
Diode | D4 | 1 | NA |  | Farnell | 1N4002 | https://uk.farnell.com/multicomp/1n4002-t/diode-standard-recovery-1a-100v/dp/2306349?st=1n4002 | 2306349 | 0.13 | 32563 | Yes | 44 | 5.72
Resistance | R1, R2, R3 | 3 | 120 | 120 OHM resistor for the LED circuit | Farnell | ERA6AEB121V | https://uk.farnell.com/panasonic/era6aeb121v/res-120r-0-125w-0805-metal-film/dp/1577646?st=0805%20resistor | 1577646 | 0.11 | 32563 | Yes | 44 | 14.52
Resistance | R4, R5 | 2 | 2k2 |  | Farnell | 1614917-1 | https://uk.farnell.com/neohm-te-connectivity/1614917-1/res-2k2-0-1-0-1w-0805-thin-film/dp/2992213?st=7.R | 2992213 | 0.15 | 32563 | Yes | 44 | 13.2
Resistance | R6 | 1 | 100k |  | Farnell | WF08U1003BTL | https://uk.farnell.com/walsin/wf08u1003btl/res-100k-0-1-100v-0805-thin-film/dp/2502861 | 2502861 | 0.18 | 32563 | Yes | 44 | 7.92
Resistance | R7 | 1 | 10 |  | Farnell | 2-1614883-3 | https://uk.farnell.com/neohm-te-connectivity/2-1614883-3/res-10r-0-1-0-1w-0805-thin-film/dp/2991936?st=0805%20resistor | 2991936 | 0.17 | 32563 | Yes | 44 | 7.48
Capacitor | C1 | 1 | 460u |  | Farnell | EEE1CA471UAP | https://uk.farnell.com/panasonic/eee1ca471uap/cap-470-f-16v-radial-smd/dp/2326124?st=470uf | 2326124 | 0.69 | 32563 | Yes | 44 | 30.36
Capacitor | C2 | 1 | 10u |  | Farnell | AVE106M16A12T-F | https://uk.farnell.com/cornell-dubilier/ave106m16a12t-f/aluminum-electrolytic-capacitor/dp/1780607 | 1780607 | 0.37 | 32563 | Yes | 44 | 16.28
Capacitor | C3, C4, C5, C6,C7, C8, C9 | 7 | 100nF |  | Farnell | C0805C104K3RACTU | https://uk.farnell.com/kemet/c0805c104k3ractu/cap-0-1-f-25v-10-x7r-0805/dp/1650863 | 1650863 | 0.05 | 32563 | Yes | 44 | 15.4
BJT NPN Transistor | Q2 | 1 | NA |  | Farnell | BC817,215 | https://uk.farnell.com/nexperia/bc817-215/transistor-npn-45v-sot-23/dp/1081223?st=bc817 | 1081223 | 0.16 | 32563 | Yes | 44 | 7.04
AVR Programming Pin | J1 | 1 | NA |  | Farnell | 826925-3 | https://uk.farnell.com/amp-te-connectivity/826925-3/header-tht-vertical-2-54mm-6way/dp/1248132 | 1248132 | 0.69 | 32563 | Yes | 44 | 30.36
Tactile Switch | SW1 | 1 | NA | Push Button | Farnell | 1301.9318.24 | https://uk.farnell.com/schurter/1301-9318-24/tactile-switch-160gf-0-05a-12vdc/dp/3586814?mckv=s_dc|pcrid|602321765887|plid||kword||match||slid||product|3586 | 3586814 | 0.42 | 32563 | Yes | 44 | 18.48
Current Sense Amplifier | IC5 | 1 | NA | Current Sense Amplifier | Mouser | MAX9928FAUA+ | https://www.mouser.co.uk/ProductDetail/Maxim-Integrated/MAX9928FAUA%2B?qs=1eQvB6Dk1vjuLd8AJ8%252BsIw%3D%3D | 2519050 | 1.79 | 32567 | Yes | 44 | 78.76
BJT PNP Transistor | Q1 | 1 | NA |  | RS Components | FMMT591TA PNP Transistor | https://uk.rs-online.com/web/p/bipolar-transistors/0274891 | 274-891 | 0.327 | 32565 | Yes | 50 | 16.35
2 way PCB terminal | J2 | 1 | NA |  | RS Components | 790-1098 | https://uk.rs-online.com/web/p/pcb-terminal-blocks/7901098 | 790-1098 | 0.512 | 32565 | Yes | 45 | 23.04
4 way PCB terminal | J4 | 1 | NA |  | RS Components | 702-0111 | https://uk.rs-online.com/web/p/pcb-headers/7020111 | 702-0111 | 0.634 | 32565 | Yes | 45 | 28.53
ATtiny85-20S | U1 | 1 | NA | Microcontroller | RS Components | ATTINY85-20SF | https://uk.rs-online.com/web/p/microcontrollers/1717852/ | 171-7852 | 1.814 | 32405 | Yes | 20 | 36.28 | Need 20 more
 |  |  |  |  |  |  |  |  |  |  |  | 955

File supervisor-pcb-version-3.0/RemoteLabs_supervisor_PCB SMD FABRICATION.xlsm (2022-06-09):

Ref | Qnty | Value | Cmp name | Footprint | Description | Vendor | Total Quantity | Q Ordered | Requisition |  | Submitted | Ordered | Delivered/Expected | surplus | Part Number | Link | Alternative Due to Stock Issues | No. of Boards
C1, C6, | 2 | 10u | cap_film_0805 | Capacitor_SMD:C_0805_2012Metric_Pad1.18x1.45mm_HandSolder | Unpolarized capacitor | farnell | 160 | 85 | 31340 |  | y | y | y | -75 | 1907513 | https://uk.farnell.com/murata/grm21bc81c106ke15l/cap-10-f-16v-10-x6s-0805/dp/1907513?ICID=I-RP-STM7REC-0 |  | 80
C1A1, C2A1, | 2 | 100p | cap_film_0805 | Capacitor_SMD:C_0805_2012Metric_Pad1.18x1.45mm_HandSolder | Unpolarized capacitor | farnell | 160 | 170 | 31258 |  | y | y | y | 10 | 2280669 | https://uk.farnell.com/avx/08055a101jat2a/cap-100pf-50v-5-c0g-np0-0805/dp/2280669?st=100p%200805 |  | 80
C2, C10 | 2 | 22u | cap_film_0805 | Capacitor_SMD:C_0805_2012Metric_Pad1.18x1.45mm_HandSolder | Unpolarized capacitor | farnell | 160 | 85 | 31340 |  | y | y | y | -75 | 2773239 | https://uk.farnell.com/kemet/c0805c226m8pactu/cap-22-f-10v-20-x5r-0805/dp/2773239?st=22uf%20mlcc |  | 80
C3, C13, | 2 | 4n7 | cap_film_0805 | Capacitor_SMD:C_0805_2012Metric_Pad1.18x1.45mm_HandSolder | Unpolarized capacitor | farnell | 160 | 170 | 31258 |  | y | y | y | 10 | 1414696 | https://uk.farnell.com/kemet/c0805c472k5ractu/cap-4700pf-50v-10-x7r-0805/dp/1414696?st=4n7%200805 |  | 80
C4, C5, C14, C15, | 4 | 9pF | cap_film_0805_mini | Capacitor_SMD:C_0805_2012Metric_Pad1.18x1.45mm_HandSolder | Unpolarized capacitor | farnell | 320 | 340 | 31258 |  | y | y | y | 20 | 1759189 | https://uk.farnell.com/multicomp/mc0805n9r0d500ct/cap-9pf-50v-c0g-np0-0805/dp/1759189?st=9pf%200805 |  | 80
C7, C17, | 2 | 1u | cap_film_0805 | Capacitor_SMD:C_0805_2012Metric_Pad1.18x1.45mm_HandSolder | POLARISED Capacitor | farnell | 160 | 174 | 31258 |  | y | y | y | 14 | 1432430 | https://uk.farnell.com/avx/tajr105k020rnj/cap-1-f-20v-10-0805-smd/dp/1432430?st=1u+0805+tantlium |  | 80
C8, C9, C11, C12, C18, C19, C21, C22, C24, C25, C26, C27, C28, C29, C30, C31, C32, C33, C34, C35, C38, C39, C40, C41, C42, C43, C1B1, C2B1, | 28 | 100n | cap_film_0805 | Capacitor_SMD:C_0805_2012Metric_Pad1.18x1.45mm_HandSolder | Unpolarized capacitor | farnell | 2240 | 2400 | 31258 |  | y | y | y | 160 | 2280669 | https://uk.farnell.com/avx/08055c104kat4a/cap-0-1-f-50v-10-x7r-0805/dp/2332787?st=100n%200805 |  | 80
D1, | 1 | BZV55B9V1 | BZV55B9V1 | Diode_SMD:D_MiniMELF | 9.1V, 500mW, 2%, Zener diode, MiniMELF | farnell | 80 | 90 | 31258 |  | y | y |  | 10 | 2319152 | https://uk.farnell.com/nexperia/bzv55-b9v1-115/diode-zener-9-1v-500mw-sod-80c/dp/2319152?st=bzv55b9v1 |  | 80
D2, D5, | 2 | PMEG6020ER | PMEG6020ER | Diode_SMD:Nexperia_CFP3_SOD-123W | 60V, 2A low Vf MEGA Schottky barrier rectifier, SOD-123W | RS Online | 160 | 200 | 31361 |  | y | y | 2022-06-06 | 40 | 780-5414 | https://uk.rs-online.com/web/p/schottky-diodes-rectifiers/7805414 |  | 80
D3, D4, | 2 | PRTR5V0U2X | PRTR5V0U2X_smaller | Package_TO_SOT_SMD:SOT-143B | Ultra low capacitance double rail-to-rail ESD protection diode, SOT-143 | farnell | 160 | 170 | 31258 |  | y | y | y | 10 | 1524157 | https://uk.farnell.com/nexperia/prtr5v0u2x-215/diode-tvs-dual-sot-143b/dp/1524157RL?st=prtr5v0u2x |  | 80
D6, | 1 | Blue LED | LED BLUE | Led_0805(2012METRIC) | Light emitting diode | farnell | 80 | 260 | 31258 |  | y | y | y | 180 | 3796324 | https://uk.farnell.com/multicomp-pro/mp008292/led-blue-210mcd-475nm-0805/dp/3796324?st=led |  | 80
D7, | 1 | Orange LED | LED ORANGE | Led_0805(2012METRIC) | Light emitting diode | farnell | 80 | 100 | 31258 |  | y | y | y | 20 | 2290332 | https://uk.farnell.com/kingbright/kp-2012seck/led-0805-250mcd-orange/dp/2290332?st=orange%20led%200805 |  | 80
D8, D9, | 2 | Yellow LED | LED | Led_0805(2012METRIC) | Light emitting diode | farnell | 160 | 170 | 31340 |  | y | y | y | 10 | 1581241 | https://uk.farnell.com/multicomp/mcl-s270yc/led-smd-0805-yellow/dp/1581241?st=0805%20yellow%20led |  | 80
EC1, EC2, EC3, EC4, EC5, EC6, EC7, EC8, | 8 | 10u | 10u | Capacitor_SMD:CP_Elec_4x5.4 | Polarized capacitor | farnell | 640 | 670 | 31258 |  | y | y | y | 30 | 2069174 | https://uk.farnell.com/kemet/exv106m025a9baa/cap-10-f-25v-radial-smd/dp/2069174?st=10uf |  | 80
EC9, EC10, EC11, | 3 | 100u | 100u | Capacitor_SMD:CP_Elec_6.3x7.7 | Polarized capacitor | farnell | 240 | 252 | 31258 |  | y | y | Y but waiting for 200 more | 12 | 2068675 | https://uk.farnell.com/kemet/edk107m035a9haa/cap-100-f-35v-radial-smd-reel/dp/2068675?st=100uf |  | 80
FB1, FB2, | 2 | BLM18PG471 | FerriteBead_Small | Inductor_SMD:L_0805_2012Metric_Pad1.05x1.20mm_HandSolder | Ferrite bead, small symbol | RS Online | 160 | 200 | 31244 |  | y | y | y | 40 | 104-8535 | https://uk.rs-online.com/web/p/ferrite-beads/1048535 |  | 80
R1, R3, | 2 | 2k2 | Resistor_0805 | Resistor_SMD:R_0805_2012Metric_Pad1.20x1.40mm_HandSolder | Resistor | farnell | 160 | 200 | 31258 |  | y | y | y | 40 | 1576464 | https://uk.farnell.com/multicomp/mchp05w4f2201t5e/res-2k2-1-0-25w-0805-thick-film/dp/1576464?st=2k2%200805 |  | 80
R2, R4, R5, R6, R37, R38, R39, | 7 | 330r | Resistor_0805 | Resistor_SMD:R_0805_2012Metric_Pad1.20x1.40mm_HandSolder | Resistor | farnell | 560 | 590 | 31258 | 31340 | y | half | half | 30 | 1576452 | https://uk.farnell.com/multicomp/mchp05w4f3300t5e/res-330r-1-0-25w-0805-thick-film/dp/1576452?st=330r%200805 |  | 80
R7, R8, R14, | 3 | 1M | Resistor_0805 | Resistor_SMD:R_0805_2012Metric_Pad1.20x1.40mm_HandSolder | Resistor | farnell | 240 | 250 | 31258 |  | y | y | y | 10 | 2861558 | https://uk.farnell.com/te-connectivity/crgcq0805f1m0/res-1m-1-0805-thick-film/dp/2861558?st=1m%200805 |  | 80
R9, R10, R11, R22, R23, R24, R25, R26, R27, R28, R29, R30, R31, R32, R33, R34, R35, R36, | 18 | 1k | Resistor_0805 | Resistor_SMD:R_0805_2012Metric_Pad1.20x1.40mm_HandSolder | Resistor | farnell | 1440 | 1520 | 31258 |  | y | y | y | 80 | 2332071 | https://uk.farnell.com/te-connectivity/crgh0805f1k0/res-1k-1-0-33w-0805-thick-film/dp/2332071?st=1k%200805 |  | 80
R12, R13, | 2 | 470r | Resistor_0805 | Resistor_SMD:R_0805_2012Metric_Pad1.20x1.40mm_HandSolder | Resistor | farnell | 160 | 170 | 31258 |  | y | y | y | 10 | 2670094 | https://uk.farnell.com/walsin/wf08p4700ftl/res-470r-1-0-25w-0805-thick-film/dp/2670094?st=470r%200805 |  | 80
R15, R16, R18, R20, | 4 | 10k | Resistor_0805 | Resistor_SMD:R_0805_2012Metric_Pad1.20x1.40mm_HandSolder | Resistor | farnell | 320 | 500 | 31258 |  | y | y | y | 180 | 2447553RL | https://uk.farnell.com/multicomp/mcwr08x1002ftl/res-10k-1-0-125w-0805-thick-film/dp/2447553RL?st=10k%200805 |  | 80
R17, R19, R21, | 3 | 2k7 | Resistor_0805 | Resistor_SMD:R_0805_2012Metric_Pad1.20x1.40mm_HandSolder | Resistor | farnell | 240 | 260 | 31258 |  | y | y | y | 20 | 2447627 | https://uk.farnell.com/multicomp/mcwr08x2701ftl/res-2k7-1-0-125w-thick-film/dp/2447627?st=2k7%200805 |  | 80
SW1, | 1 | Stepper_Mode | SW_DIP_x03 | Button_Switch_SMD:SW_DIP_SPSTx03_Slide_6.7x9.18mm_W6.73mm_P2.54mm_LowProfile_JPin | 3x DIP Switch, Single Pole Single Throw (SPST) switch, small symbol | farnell | 80 | 90 | 31258 |  | y | n | 2022-09-15 | 10 | 3778050 | https://uk.farnell.com/cts/219-3lpstr/dip-switch-0-1a-50vdc-3pos-smd/dp/3778050?st=dipswitches |  | 80
SW2, SW3, | 2 | Student Reset | pushbutton_tactile_2pin_SMD |  | MEC 5E single pole normally-open tactile switch | farnell | 160 | 170 | 31258 |  | y | y | y | 10 | 2320087RL | https://uk.farnell.com/c-k-components/pts645sm43smtr92lfs/switch-spst-0-05a-12vdc-smd-4/dp/2320087RL |  | 80
 |  |  |  |  |  |  | 0 |  |  |  |  |  |  | 0 |  |  |  | 80
U3, | 1 | AMS1117-3.3 | AMS1117-3.3 | Package_TO_SOT_SMD:SOT-223-3_TabPin2 | 1A Low Dropout regulator, positive, 3.3V fixed output, SOT-223 | farnell | 80 | 100 | 31258 |  | y | y | y | 20 | 1652366RL | https://uk.farnell.com/on-semiconductor/ncp1117st33t3g/ic-linear-voltage-regulator/dp/1652366RL?st=ldo |  | 80
U4, U6, | 2 | ATSAMD21G18A-M | ATSAMD21G18A-M | Package_DFN_QFN:QFN-48-1EP_7x7mm_P0.5mm_EP5.15x5.15mm | SAM D21 Microchip SMART ARM-based Flash MCU, 48Mhz, 256K Flash, 32K SRAM, QFN-48 |  | 160 | 0 | not req |  | n | n | NOT REQUIRED |  |  |  |  | 80
U5, U7, | 2 | 4094 | 4094 | Package_DIP:SMDIP-18_W9.53mm | 8-bit serial in/out Shift Register 3-State Outputs | farnell | 160 | 170 | 31258 |  | y | y | y | 10 | 1201297 | https://uk.farnell.com/nexperia/hef4094bt/ic-4000-locmos-smd-4094-soic16/dp/1201297?st=4094 | https://www.mouser.co.uk/ProductDetail/Nexperia/HEF4094BT653?qs=me8TqzrmIYXYasToWufdKw%3D%3D | 80
U8, | 1 | 4069 | 4069 | Package_DIP:SMDIP-14_W9.53mm | Hex inverter | farnell | 80 | 100 | 31258 |  | y | y | y | 20 | 1201295 | https://uk.farnell.com/nexperia/hef4069ubt/ic-4000-locmos-smd-4069-soic14/dp/1201295?st=4069 |  | 80
U9, U10, U11, U12, | 4 | 4081 | 4081 | Package_DIP:SMDIP-14_W9.53mm | Quad And 2 inputs | farnell | 320 | 340 | 31258 |  | y | y | y | 20 | 1085290 | https://uk.farnell.com/nexperia/hef4081bt/ic-4000-locmos-smd-4081-soic14/dp/1085290?st=4081 |  | 80
U13, U14, | 2 | 74HC86 | 74HC86 | Package_DIP:SMDIP-14_W9.53mm | Quad 2-input XOR | farnell | 160 | 170 | 31258 |  | y | y | y | 10 | 1085331 | https://uk.farnell.com/nexperia/74hc86d/ic-74hc-cmos-smd-74hc86-soic14/dp/1085331?st=74hc86 |  | 80
U15, U16, U17, | 3 | NCS20074D | NCS20074D | Package_SO:SOIC-14_3.9x8.7mm_P1.27mm | Quad, 2.8V/Ã‚Âµs, Rail-to-Rail Output, SOIC-14 | farnell | 240 | 252 | 31258 |  | y | y | N | 12 | 2774608 | https://uk.farnell.com/on-semiconductor/ncs20074dr2g/op-amp-quad-3mhz-2-8v-us-soic/dp/2774608?st=ncs20074 |  | 80
U1, U18, | 2 | R-78C5.0-1.0 | R-78C5.0-1.0 | Converter_DCDC:Converter_DCDC_RECOM_R-78E-0.5_THT | 1A Step-Down DC/DC-Regulator, 7-42V input, 5V fixed Output Voltage, LM78xx replacement, -40Ã‚Â°C to +85Ã‚Â°C, SIP3 | RS Online | 160 | 84 | 31361 |  | y | y | y | -76 | 193-4004 | https://uk.rs-online.com/web/p/switching-regulators/1934004 |  | 80
U19, | 1 | AD8497 | AD8497 | Package_SO:MSOP-8_3x3mm_P0.65mm | Precision Thermocouple Amplifiers with Cold Junction Compensation, K-Type Thermocouple, 25 to 100C, MSOP-8 |  | 80 | 0 |  |  | n | n | NOT AVAILABLE |  |  |  |  | 80
U20, U21, U22, | 3 | 74LS07 | 74LS07 | SOIC-14 | Hex Buffers and Drivers With Open Collector High Voltage Outputs | RS Online | 240 | 250 | 31244 |  | y | y | y | 10 | 827-0301 | https://uk.rs-online.com/web/p/buffers/8270301 |  | 80
Y1, Y2, | 2 | 32.768 kHz | Crystal_Small | Crystal:Crystal_SMD_SeikoEpson_MC405-2Pin_9.6x4.1mm_HandSoldering | Two pin crystal, small symbol | farnell | 160 | 170 | 31258 |  | y | y | y | 10 | 2467903 | https://uk.farnell.com/abracon/asek-32-768khz-lrt/osc-32-768khz-3-2-x-2-5mm-lvcmos/dp/2467903 |  | 80
 |  |  |  |  |  |  | 0 |  |  |  |  |  |  | 0 |  |  |  | 80
 |  |  |  |  |  |  | 0 |  |  |  |  |  |  |  |  |  |  | 80
 |  |  |  |  |  |  | 0 |  |  |  |  |  |  |  |  |  |  | 80
 |  |  |  | Added Stuff To Include |  |  | 0 |  |  |  |  |  |  |  |  |  |  | 80
 |  |  |  |  |  |  | 0 |  |  |  |  |  |  |  |  |  |  | 80
 |  |  |  | https://www.digikey.be/en/products/detail/toshiba-semiconductor-and-storage/TC7SH14FLJ-CT/4971175 |  |  | 0 |  |  |  |  |  |  |  |  |  |  | 80
 |  |  |  | 10n Cap |  |  | 0 |  |  |  |  |  |  |  |  |  |  | 80
 |  |  |  | 0r Resistor |  |  | 0 |  |  |  |  |  |  |  |  |  |  | 80
 |  |  |  | Extra Caps |  |  | 0
 |  |  |  |  |  |  | 0
 |  |  |  |  |  |  | 0
 |  |  |  | Only needed for oscillator so not 100% req at this moment

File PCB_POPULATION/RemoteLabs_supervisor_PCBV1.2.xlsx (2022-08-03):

Ref | Quantity | Value | Component Name | Footprint | Description | Vendor
A1, A2, | 2 | Arduino_Nano_33_IoT | Arduino_Nano_33_IoT | Module:Arduino_Nano | Arduino Nano v2.x
A3, | 1 | Infineon Motor Shield Uno | Infineon Motor Shield MOD | Module:Infineon Motor Sheild hiddenPins | Infineon Motor Driver Shield for Arduino Uno
A4, | 1 | DRV8825 Stepper Driver | DRV8825 High Current Stepper Motor Driver Module | Module:DRV8825 Stepper Motor Module | DRV8825 High Current Stepper Motor Driver Module
A5, | 1 | LM2596S DC-DC Module | LM2596S DC-DC Module | Module:LM2596S DC-DC Module | 5V 3A Step-Down Voltage Regulator, TO-263
C1, C6, | 2 | 10u | cap_film_0805 | Capacitor_SMD:C_0805_2012Metric_Pad1.18x1.45mm_HandSolder | Unpolarized capacitor
C1A1, | 1 | 100p | cap_film_0805 | Capacitor_SMD:C_0805_2012Metric_Pad1.18x1.45mm_HandSolder | Unpolarized capacitor
C1B1, | 1 | 100n | cap_film_0805 | Capacitor_SMD:C_0805_2012Metric_Pad1.18x1.45mm_HandSolder | Unpolarized capacitor
C2, C10, | 2 | 22u | cap_film_0805 | Capacitor_SMD:C_0805_2012Metric_Pad1.18x1.45mm_HandSolder | Unpolarized capacitor
C2A1, | 1 | 100p | cap_film_0805 | Capacitor_SMD:C_0805_2012Metric_Pad1.18x1.45mm_HandSolder | Unpolarized capacitor
C2B1, | 1 | 100n | cap_film_0805 | Capacitor_SMD:C_0805_2012Metric_Pad1.18x1.45mm_HandSolder | Unpolarized capacitor
C3, C13, | 2 | 4n7 | cap_film_0805 | Capacitor_SMD:C_0805_2012Metric_Pad1.18x1.45mm_HandSolder | Unpolarized capacitor
C4, C8, C9, C11, C12, C16, C18, C19, C21, C22, C24, C25, C26, C27, C28, C29, C30, C31, C32, C33, C34, C35, C38, C39, C40, C41, C42, C43, | 28 | 100n | cap_film_0805 | Capacitor_SMD:C_0805_2012Metric_Pad1.18x1.45mm_HandSolder | Unpolarized capacitor
C7, C17, | 2 | 1u | tantalum | Capacitor_Tantalum_SMD:CP_EIA-2012-12_Kemet-R_Pad1.30x1.05mm_HandSolder | Polarized capacitor
D1, | 1 | BZV55B9V1 | BZV55B9V1 | Diode_SMD:D_MiniMELF | 9.1V, 500mW, 2%, Zener diode, MiniMELF
D2, D5, | 2 | PMEG6020ER | PMEG6020ER | Diode_SMD:Nexperia_CFP3_SOD-123W | 60V, 2A low Vf MEGA Schottky barrier rectifier, SOD-123W
D3, D4, | 2 | PRTR5V0U2X | PRTR5V0U2X_smaller | Package_TO_SOT_SMD:SOT-143 | Ultra low capacitance double rail-to-rail ESD protection diode, SOT-143
D6, | 1 | 12V Power | LED | Diode_SMD:D_0805_2012Metric_Pad1.15x1.40mm_HandSolder | Light emitting diode
D7, | 1 | 3V3 Power | LED | Diode_SMD:D_0805_2012Metric_Pad1.15x1.40mm_HandSolder | Light emitting diode
D8, D9, | 2 | Yellow | LED | Diode_SMD:D_0805_2012Metric_Pad1.15x1.40mm_HandSolder | Light emitting diode
EC1, EC2, EC3, EC4, EC5, EC6, EC7, EC8, | 8 | 10u | 22u | Capacitor_SMD:CP_Elec_4x5.4 | Polarized capacitor
EC9, EC10, EC11, EC12, | 4 | 100u | 100u | Capacitor_SMD:CP_Elec_6.3x7.7 | Polarized capacitor
F1, | 1 | 20A | Fuse | Fuse:Fuseholder_Cylinder-5x20mm_Stelvio-Kontek_PTF78_Horizontal_Open | Fuse
F2, | 1 | 2A | Fuse | Fuse:Fuseholder_Cylinder-5x20mm_Stelvio-Kontek_PTF78_Horizontal_Open | Fuse
FB1, FB2, | 2 | BLM18PG471 | FerriteBead_Small | Inductor_SMD:L_0805_2012Metric_Pad1.05x1.20mm_HandSolder | Ferrite bead, small symbol
J1, | 1 | Super_Prog_Header | Molex_5pin_2.54mm_M | Connector_Molex:Molex_KK-254_AE-6410-05A_1x05_P2.54mm_Vertical | Generic connector, single row, 01x05, script generated (kicad-library-utils/schlib/autogen/connector/)
J2, | 1 | WS2821B LEDs | 3pin_molex_2.54mm_male | Connector_Molex:Molex_KK-254_AE-6410-03A_1x03_P2.54mm_Vertical | Generic connector, single row, 01x03, script generated (kicad-library-utils/schlib/autogen/connector/)
J3, | 1 | XT60_60A_male | XT60_60A_male | Connector_AMASS:AMASS_XT60PW-M | Generic connector, single row, 01x02, script generated (kicad-library-utils/schlib/autogen/connector/)
J4, | 1 | Strip Lighting | 2pin_molex_2.54mm_male | Connector_Molex:Molex_KK-254_AE-6410-02A_1x02_P2.54mm_Vertical | Generic connector, single row, 01x02, script generated (kicad-library-utils/schlib/autogen/connector/)
J5, | 1 | USB_A_Stacked | USB_A_Stacked | Connector_USB:USB_A_Wuerth_61400826021_Horizontal_Stacked | USB Type A connector, stacked
J6, | 1 | 5V_DC_LED | Screw_Terminal_01x02 | TerminalBlock:TerminalBlock_Altech_AK300-2_P5.00mm | Generic screw terminal, single row, 01x02, script generated (kicad-library-utils/schlib/autogen/connector/)
J7, J13, | 2 | USB_B_Mini | USB_B_Mini | Connector_USB:USB_Mini-B_Lumberg_2486_01_Horizontal | USB Mini Type B connector
J16, | 1 | DC Motor PWR | Screw_Terminal_01x02 | TerminalBlock:TerminalBlock_Altech_AK300-2_P5.00mm | Generic screw terminal, single row, 01x02, script generated (kicad-library-utils/schlib/autogen/connector/)
J17, | 1 | MotorController Output | Screw_Terminal_01x03 | TerminalBlock:TerminalBlock_Altech_AK300-3_P5.00mm | Generic screw terminal, single row, 01x03, script generated (kicad-library-utils/schlib/autogen/connector/)
J18, | 1 | DC Motor Output | Screw_Terminal_01x03 | TerminalBlock:TerminalBlock_Altech_AK300-3_P5.00mm | Generic screw terminal, single row, 01x03, script generated (kicad-library-utils/schlib/autogen/connector/)
J19, | 1 | Stepper Motor Output | 4_pin_JST_XH_male | Connector_JST:JST_XH_B4B-XH-A_1x04_P2.50mm_Vertical | Generic connector, single row, 01x04, script generated (kicad-library-utils/schlib/autogen/connector/)
J20, | 1 | Servo_A | Conn_01x03_Male | Connector_PinHeader_2.54mm:PinHeader_1x03_P2.54mm_Vertical | Generic connector, single row, 01x03, script generated (kicad-library-utils/schlib/autogen/connector/)
J21, | 1 | Servo_B | Conn_01x03_Male | Connector_PinHeader_2.54mm:PinHeader_1x03_P2.54mm_Vertical | Generic connector, single row, 01x03, script generated (kicad-library-utils/schlib/autogen/connector/)
J22, | 1 | Thermocouple | Screw_Terminal_01x02 | TerminalBlock:TerminalBlock_Altech_AK300-2_P5.00mm | Generic screw terminal, single row, 01x02, script generated (kicad-library-utils/schlib/autogen/connector/)
J23, | 1 | limit_switch_A | 2pin_molex_2.54mm_male | Connector_Molex:Molex_KK-254_AE-6410-02A_1x02_P2.54mm_Vertical | Generic connector, single row, 01x02, script generated (kicad-library-utils/schlib/autogen/connector/)
J25, | 1 | Optical Encoder | Molex_5pin_2.54mm_M | Connector_Molex:Molex_KK-254_AE-6410-05A_1x05_P2.54mm_Vertical | Generic connector, single row, 01x05, script generated (kicad-library-utils/schlib/autogen/connector/)
J26, | 1 | Student_Prog_Header | Molex_5pin_2.54mm_M | Connector_Molex:Molex_KK-254_AE-6410-05A_1x05_P2.54mm_Vertical | Generic connector, single row, 01x05, script generated (kicad-library-utils/schlib/autogen/connector/)
J30, | 1 | 12V_DC | Screw_Terminal_01x02 | TerminalBlock:TerminalBlock_Altech_AK300-2_P5.00mm | Generic screw terminal, single row, 01x02, script generated (kicad-library-utils/schlib/autogen/connector/)
J31, | 1 | 5V_DC_RPI | Screw_Terminal_01x02 | TerminalBlock:TerminalBlock_Altech_AK300-2_P5.00mm | Generic screw terminal, single row, 01x02, script generated (kicad-library-utils/schlib/autogen/connector/)
Q1, | 1 | IRF5305_PBF | IRF5305_PBF | Package_TO_SOT_THT:TO-220-3_Vertical | -31A Id, -55V Vds, Single P-Channel HEXFET Power MOSFET, 60mOhm Ron, TO-220AB
R1, R3, | 2 | 2k2 | Resistor_0805 | Resistor_SMD:R_0805_2012Metric_Pad1.20x1.40mm_HandSolder | Resistor
R2, R4, R5, R6, R37, R38, R39, | 7 | 330r | Resistor_0805 | Resistor_SMD:R_0805_2012Metric_Pad1.20x1.40mm_HandSolder | Resistor
R7, R8, R14, | 3 | 1M | Resistor_0805 | Resistor_SMD:R_0805_2012Metric_Pad1.20x1.40mm_HandSolder | Resistor
R9, R10, R11, R22, R23, R24, R25, R26, R27, R28, R29, R30, R31, R32, R33, R34, R35, | 17 | 1k | Resistor_0805 | Resistor_SMD:R_0805_2012Metric_Pad1.20x1.40mm_HandSolder | Resistor
R12, R13, | 2 | 470r | Resistor_0805 | Resistor_SMD:R_0805_2012Metric_Pad1.20x1.40mm_HandSolder | Resistor
R15, R16, R18, R20, R36, | 5 | 10k | Resistor_0805 | Resistor_SMD:R_0805_2012Metric_Pad1.20x1.40mm_HandSolder | Resistor
R17, R19, R21, | 3 | 2k7 | Resistor_0805 | Resistor_SMD:R_0805_2012Metric_Pad1.20x1.40mm_HandSolder | Resistor
SW1, | 1 | Stepper_Mode | SW_DIP_x03 | Button_Switch_SMD:SW_DIP_SPSTx03_Slide_6.7x9.18mm_W6.73mm_P2.54mm_LowProfile_JPin | 3x DIP Switch, Single Pole Single Throw (SPST) switch, small symbol
SW2, | 1 | Student Reset | pushbutton_tactile_2pin_SMD | Button_Switch_SMD:SW_Push_1P1T_NO_CK_KSC6xxJ | MEC 5E single pole normally-open tactile switch
SW3, | 1 | Supervisor Reset | pushbutton_tactile_2pin_SMD | Button_Switch_SMD:SW_Push_1P1T_NO_CK_KSC6xxJ | MEC 5E single pole normally-open tactile switch
U1, U18, | 2 | R-78C5.0-1.0 | R-78C5.0-1.0 | Converter_DCDC:Converter_DCDC_RECOM_R-78E-0.5_THT | 1A Step-Down DC/DC-Regulator, 7-42V input, 5V fixed Output Voltage, LM78xx replacement, -40Ã‚Â°C to +85Ã‚Â°C, SIP3
U3, | 1 | AMS1117-3.3 | AMS1117-3.3 | Package_TO_SOT_SMD:SOT-223-3_TabPin2 | 1A Low Dropout regulator, positive, 3.3V fixed output, SOT-223
U4, U6, | 2 | ATSAMD21G18A-M | ATSAMD21G18A-M | Package_DFN_QFN:QFN-48-1EP_7x7mm_P0.5mm_EP5.15x5.15mm | SAM D21 Microchip SMART ARM-based Flash MCU, 48Mhz, 256K Flash, 32K SRAM, QFN-48
U5, U7, | 2 | 4094 | 4094 | Package_SO:SOIC-16_3.9x9.9mm_P1.27mm | 8-bit serial in/out Shift Register 3-State Outputs
U8, | 1 | 4069 | 4069_4 | Package_SO:SOIC-14_3.9x8.7mm_P1.27mm | Hex inverter
U9, U10, U11, U12, | 4 | 4081 | 4081_5 | Package_SO:SOIC-14_3.9x8.7mm_P1.27mm | Quad And 2 inputs
U13, U14, | 2 | 74HC86 | 74HC86_9 | Package_SO:SOIC-14_3.9x8.7mm_P1.27mm | Quad 2-input XOR
U15, U16, U17, | 3 | NCS20074D | NCS20074D | Package_SO:SOIC-14_3.9x8.7mm_P1.27mm | Quad, 2.8V/Ã‚Âµs, Rail-to-Rail Output, SOIC-14
U20, U21, U22, | 3 | 74LS07 | 74LS07 | Package_SO:SOIC-14_3.9x8.7mm_P1.27mm | Hex Buffers and Drivers With Open Collector High Voltage Outputs
X1, X2, | 2 | 32.768kHz | ASEK-xxxMHz | Oscillator:Oscillator_SMD_Abracon_ASE-4Pin_3.2x2.5mm | 3.3V CMOS SMD Crystal Clock Oscillator, Abracon

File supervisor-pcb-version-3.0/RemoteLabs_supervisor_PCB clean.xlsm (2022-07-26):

Ref | Qnty | Value | Cmp name | Footprint | Description | Vendor | Total Quantity | Q Ordered | Requisition |  | Submitted | Ordered | Delivered/Expected | surplus | Part Number | Link | Alternative Due to Stock Issues | No. of Boards
A1, A2, | 2 | Arduino_Nano_33_IoT | Arduino_Nano_33_IoT | Module:Arduino_Nano | Arduino Nano v2.x | RS Online | 160 | 160 | 31244 |  | y | y | y | 0 | 192-7585 | https://uk.rs-online.com/web/p/arduino/1927585 |  | 80
A3, | 1 | Infineon Motor Shield Uno | Infineon Motor Shield Uno | Module:Arduino_UNO_R3 | Arduino UNO Microcontroller Module, release 3 | RS Online | 80 | 80 | 31244 |  | y | y | 2022-05-24 | 0 | 906-2874 | https://uk.rs-online.com/web/p/shields-for-arduino/9062874 |  | 80
A4, | 1 | DRV8825 High Current Stepper Motor Driver Module | DRV8825 High Current Stepper Motor Driver Module | Dual Pin Headers - Custom | DRV8825 High Current Stepper Motor Driver Module | az-delivery | 80 | 80 | 31338 |  | y | y | 2022-06-19 | 0 |  | https://www.az-delivery.de/en/products/drv8825-schrittmotor-treiber-modul-mit-kuhlkorper?variant=37100118866 |  | 80
A5, | 1 | LM2596S DC-DC Module | LM2596S DC-DC Module | 4 Pin Custom Module | 5V 3A Step-Down Voltage Regulator, TO-263 | az-delivery | 80 | 80 | 31338 |  | y | y | 2022-06-19 | 0 |  | https://www.az-delivery.de/en/products/lm2596s-dc-dc-step-down-modul-1 |  | 80
C1, C6, | 2 | 10u | cap_film_0805 | Capacitor_SMD:C_0805_2012Metric_Pad1.18x1.45mm_HandSolder | Unpolarized capacitor | farnell | 160 | 85 | 31340 |  | y | y | y | -75 | 1907513 | https://uk.farnell.com/murata/grm21bc81c106ke15l/cap-10-f-16v-10-x6s-0805/dp/1907513?ICID=I-RP-STM7REC-0 |  | 80
C1A1, C2A1, | 2 | 100p | cap_film_0805 | Capacitor_SMD:C_0805_2012Metric_Pad1.18x1.45mm_HandSolder | Unpolarized capacitor | farnell | 160 | 170 | 31258 |  | y | y | y | 10 | 2280669 | https://uk.farnell.com/avx/08055a101jat2a/cap-100pf-50v-5-c0g-np0-0805/dp/2280669?st=100p%200805 |  | 80
C2, C10 | 2 | 22u | cap_film_0805 | Capacitor_SMD:C_0805_2012Metric_Pad1.18x1.45mm_HandSolder | Unpolarized capacitor | farnell | 160 | 85 | 31340 |  | y | y | y | -75 | 2773239 | https://uk.farnell.com/kemet/c0805c226m8pactu/cap-22-f-10v-20-x5r-0805/dp/2773239?st=22uf%20mlcc |  | 80
C3, C13, | 2 | 4n7 | cap_film_0805 | Capacitor_SMD:C_0805_2012Metric_Pad1.18x1.45mm_HandSolder | Unpolarized capacitor | farnell | 160 | 170 | 31258 |  | y | y | y | 10 | 1414696 | https://uk.farnell.com/kemet/c0805c472k5ractu/cap-4700pf-50v-10-x7r-0805/dp/1414696?st=4n7%200805 |  | 80
C4, C5, C14, C15, | 4 | 9pF | cap_film_0805_mini | Capacitor_SMD:C_0805_2012Metric_Pad1.18x1.45mm_HandSolder | Unpolarized capacitor | farnell | 320 | 340 | 31258 |  | y | y | y | 20 | 1759189 | https://uk.farnell.com/multicomp/mc0805n9r0d500ct/cap-9pf-50v-c0g-np0-0805/dp/1759189?st=9pf%200805 |  | 80
C7, C17, | 2 | 1u | cap_film_0805 | Capacitor_SMD:C_0805_2012Metric_Pad1.18x1.45mm_HandSolder | POLARISED Capacitor | farnell | 160 | 174 | 31258 |  | y | y | y | 14 | 1432430 | https://uk.farnell.com/avx/tajr105k020rnj/cap-1-f-20v-10-0805-smd/dp/1432430?st=1u+0805+tantlium |  | 80
C8, C9, C11, C12, C18, C19, C21, C22, C24, C25, C26, C27, C28, C29, C30, C31, C32, C33, C34, C35, C38, C39, C40, C41, C42, C43, C1B1, C2B1, | 28 | 100n | cap_film_0805 | Capacitor_SMD:C_0805_2012Metric_Pad1.18x1.45mm_HandSolder | Unpolarized capacitor | farnell | 2240 | 2400 | 31258 |  | y | y | y | 160 | 2280669 | https://uk.farnell.com/avx/08055c104kat4a/cap-0-1-f-50v-10-x7r-0805/dp/2332787?st=100n%200805 |  | 80
D1, | 1 | BZV55B9V1 | BZV55B9V1 | Diode_SMD:D_MiniMELF | 9.1V, 500mW, 2%, Zener diode, MiniMELF | farnell | 80 | 90 | 31258 |  | y | y |  | 10 | 2319152 | https://uk.farnell.com/nexperia/bzv55-b9v1-115/diode-zener-9-1v-500mw-sod-80c/dp/2319152?st=bzv55b9v1 |  | 80
D2, D5, | 2 | PMEG6020ER | PMEG6020ER | Diode_SMD:Nexperia_CFP3_SOD-123W | 60V, 2A low Vf MEGA Schottky barrier rectifier, SOD-123W | RS Online | 160 | 200 | 31361 |  | y | y | 2022-06-06 | 40 | 780-5414 | https://uk.rs-online.com/web/p/schottky-diodes-rectifiers/7805414 |  | 80
D3, D4, | 2 | PRTR5V0U2X | PRTR5V0U2X_smaller | Package_TO_SOT_SMD:SOT-143B | Ultra low capacitance double rail-to-rail ESD protection diode, SOT-143 | farnell | 160 | 170 | 31258 |  | y | y | y | 10 | 1524157 | https://uk.farnell.com/nexperia/prtr5v0u2x-215/diode-tvs-dual-sot-143b/dp/1524157RL?st=prtr5v0u2x |  | 80
D6, | 1 | Blue LED | LED BLUE | Led_0805(2012METRIC) | Light emitting diode | farnell | 80 | 260 | 31258 |  | y | y | y | 180 | 3796324 | https://uk.farnell.com/multicomp-pro/mp008292/led-blue-210mcd-475nm-0805/dp/3796324?st=led |  | 80
D7, | 1 | Orange LED | LED ORANGE | Led_0805(2012METRIC) | Light emitting diode | farnell | 80 | 100 | 31258 |  | y | y | y | 20 | 2290332 | https://uk.farnell.com/kingbright/kp-2012seck/led-0805-250mcd-orange/dp/2290332?st=orange%20led%200805 |  | 80
D8, D9, | 2 | Yellow LED | LED | Led_0805(2012METRIC) | Light emitting diode | farnell | 160 | 170 | 31340 |  | y | y | y | 10 | 1581241 | https://uk.farnell.com/multicomp/mcl-s270yc/led-smd-0805-yellow/dp/1581241?st=0805%20yellow%20led |  | 80
EC1, EC2, EC3, EC4, EC5, EC6, EC7, EC8, | 8 | 10u | 10u | Capacitor_SMD:CP_Elec_4x5.4 | Polarized capacitor | farnell | 640 | 670 | 31258 |  | y | y | y | 30 | 2069174 | https://uk.farnell.com/kemet/exv106m025a9baa/cap-10-f-25v-radial-smd/dp/2069174?st=10uf |  | 80
EC9, EC10, EC11, | 3 | 100u | 100u | Capacitor_SMD:CP_Elec_6.3x7.7 | Polarized capacitor | farnell | 240 | 252 | 31258 |  | y | y | Y but waiting for 200 more | 12 | 2068675 | https://uk.farnell.com/kemet/edk107m035a9haa/cap-100-f-35v-radial-smd-reel/dp/2068675?st=100uf |  | 80
F1, F2, | 2 | 20A | Fuse | Fuse:Fuseholder_Cylinder-5x20mm_Stelvio-Kontek_PTF78_Horizontal_Open | Fuse | farnell | 160 | 168 | 31258 |  | y | y | y | 8 | 1597013 | https://uk.farnell.com/littelfuse/65600001009/fuseholder-5x20mm-pcb-mount/dp/1597013 |  | 80
FB1, FB2, | 2 | BLM18PG471 | FerriteBead_Small | Inductor_SMD:L_0805_2012Metric_Pad1.05x1.20mm_HandSolder | Ferrite bead, small symbol | RS Online | 160 | 200 | 31244 |  | y | y | y | 40 | 104-8535 | https://uk.rs-online.com/web/p/ferrite-beads/1048535 |  | 80
 |  |  |  |  |  |  | 0 |  |  |  |  |  |  | 0 |  |  |  | 80
Pin Headers
J29, | 1 | 3 Pin Header | Conn_01x03_Male | Connector_PinHeader_2.54mm:PinHeader_1x03_P2.54mm_Vertical | Generic Pin Header | farnell | 80 | 100 | 31258 |  | y | y | y | 20 | 1022248 | https://uk.farnell.com/harwin/m20-9990345/header-straight-2-54mm-1row-3way/dp/1022248?st=2.54mm%20pin%20header |  | 80
Generic M | 6 | Pin Headers | Pin Header, Board-to-Board, 2.54 mm, 1 Rows, 20 Contacts, Through Hole, M20 | Connector_PinHeader_2.54mm:PinHeader_1x05_P2.54mm_Vertical | Generic Pin Header | farnell | 480 | 500 | 31258 |  | y | y | y | 20 | 1022262 | https://uk.farnell.com/harwin/m20-9992046/header-1row-20way/dp/1022262 |  | 80
Generic F | 6 | Pin Sockets | PCB Receptacle, Board-to-Board, 2.54 mm, 1 Rows, 20 Contacts, Through Hole Mount, 2212S | Connector_PinHeader_2.54mm:PinHeader_1x08_P2.54mm_Vertical | Generic Pin Header | farnell | 480 | 500 | 31258 |  | y | y | y | 20 | 1593469 | https://uk.farnell.com/multicomp/2212s-20sg-85/socket-pcb-1-row-20way/dp/1593469 |  | 80
 |  |  |  |  |  |  | 0 |  |  |  |  |  |  | 0
Connectors |  |  |  |  |  |  | 0 |  |  |  |  |  |  | 0 |  |  |  | 80
J1, J25, J26, | 3 | 5 Pin Molex, Wire-to-Board, 2.54 mm, 1 Rows, 5 Contacts, Through Hole Straight | Conn_01x05_Male | Connector_PinHeader_2.54mm:PinHeader_1x05_P2.54mm_Vertical | MOLEX 5 PIN 2.54mm | farnell | 240 | 252 | 31258 |  | y | y | y | 12 | 9731679 | https://uk.farnell.com/molex/22-27-2051/connector-header-5pos-1row-2-54mm/dp/9731679?st=2.54mm%20pin%20header |  | 80
J3, | 1 | XT45_connector_DC_45A_male | XT45_connector_DC_45A_male | Connector_AMASS:AMASS_XT45PW-M | Generic connector, single row, 01x02, script generated (kicad-library-utils/schlib/autogen/connector/) | RS Online | 80 | 80 | 31244 |  | y | y | y | 0 | 180-5375 | https://uk.rs-online.com/web/p/compact-power-connectors/1805375 |  | 80
J5, | 1 | USB_A_Stacked | 2784974 |  | USB Type A connector, stacked | farnell | 80 | 100 | 31258 |  | y | y | y | 20 | 2784974 | https://uk.farnell.com/gct-global-connector-technology/usb1035-gf-p-0-b-b/usb-conn-dual-rcpt-2-0-2port-8pos/dp/2784974?st=usb%20a |  | 80
J7, J13, | 2 | USB_B_Mini | 2293774 | Connector_USB:USB_Mini-B_Lumberg_2486_01_Horizontal | USB Mini Type B connector | farnell | 160 | 170 | 31258 |  | y | y | y | 10 | 2293774 | https://uk.farnell.com/gct-global-connector-technology/usb2066-05-rbhm-15-stb-00-00-a/mini-usb-2-0-type-b-receptacle/dp/2293774?st=usb%20a |  | 80
J16, J22, J30, J31, | 4 | 2 pin Screw terminal | 2008019 | TerminalBlock:TerminalBlock_Altech_AK300-2_P5.00mm | Generic screw terminal, single row, 01x02, script generated (kicad-library-utils/schlib/autogen/connector/) | farnell | 320 | 335 | 31258 |  | y | y | y | 15 | 2008019 | https://uk.farnell.com/multicomp/mc000048/terminal-block-wire-to-brd-2pos/dp/2008019?st=screw%20terminal%20block |  | 80
J17, J18, | 2 | 3 pin screw terminal | 2008020 | TerminalBlock:TerminalBlock_Altech_AK300-3_P5.00mm | Generic screw terminal, single row, 01x03, script generated (kicad-library-utils/schlib/autogen/connector/) | farnell | 160 | 170 | 31258 |  | y | y | y | 10 | 2008020 | https://uk.farnell.com/multicomp/mc000049/terminal-block-wire-to-brd-3pos/dp/2008020?st=screw%20terminal%20block |  | 80
J4, J23, J24, | 3 | 2 pin Molex | 1462926 | Connector_PinHeader_2.54mm:PinHeader_1x02_P2.54mm_Vertical | MOLEX 2 PIN 2.54mm | farnell | 240 | 250 | 31258 |  | y | y | y | 10 | 1462926 | e (https://uk.farnell.com/molex/22-23-2021/connector-header-2pos-1row-2-54mm/dp/1462926) |  | 80
J2, J20, J21, | 3 | 3 pin Molex | 1462950 | Connector_PinHeader_2.54mm:PinHeader_1x03_P2.54mm_Vertical | MOLEX 3 PIN 2.54mm | farnell | 240 | 250 | 31258 |  | y | y | y | 10 | 1462950 | https://uk.farnell.com/molex/22-23-2031/connector-header-3pos-1row-2-54mm/dp/1462950?st=2.54mm%20pin%20header%203%20pin |  | 80
J19, | 1 | 4 Pin JST XH |  | Connector_PinHeader_2.54mm:PinHeader_1x04_P2.54mm_Vertical | Generic connector, single row, 01x04, script generated (kicad-library-utils/schlib/autogen/connector/) | RS Online | 80 | 80 | 31244 |  | y | y | y | 0 | 820-1551 | https://uk.rs-online.com/web/p/pcb-headers/8201551 |  | 80
 |  |  |  |  |  |  | 0 |  |  |  |  |  |  | 0 |  |  |  | 80
Q1, | 1 | IRF5305_PBF | IRF5305_PBF | Package_TO_SOT_THT:TO-220-3_Vertical | -31A Id, -55V Vds, Single P-Channel HEXFET Power MOSFET, 60mOhm Ron, TO-220AB | farnell | 80 | 100 | 31258 |  | y | y | y | 20 | 8648255 | https://uk.farnell.com/infineon/irf5305pbf/mosfet-p-55v-31a-to-220/dp/8648255 |  | 80
R1, R3, | 2 | 2k2 | Resistor_0805 | Resistor_SMD:R_0805_2012Metric_Pad1.20x1.40mm_HandSolder | Resistor | farnell | 160 | 200 | 31258 |  | y | y | y | 40 | 1576464 | https://uk.farnell.com/multicomp/mchp05w4f2201t5e/res-2k2-1-0-25w-0805-thick-film/dp/1576464?st=2k2%200805 |  | 80
R2, R4, R5, R6, R37, R38, R39, | 7 | 330r | Resistor_0805 | Resistor_SMD:R_0805_2012Metric_Pad1.20x1.40mm_HandSolder | Resistor | farnell | 560 | 590 | 31258 | 31340 | y | half | half | 30 | 1576452 | https://uk.farnell.com/multicomp/mchp05w4f3300t5e/res-330r-1-0-25w-0805-thick-film/dp/1576452?st=330r%200805 |  | 80
R7, R8, R14, | 3 | 1M | Resistor_0805 | Resistor_SMD:R_0805_2012Metric_Pad1.20x1.40mm_HandSolder | Resistor | farnell | 240 | 250 | 31258 |  | y | y | y | 10 | 2861558 | https://uk.farnell.com/te-connectivity/crgcq0805f1m0/res-1m-1-0805-thick-film/dp/2861558?st=1m%200805 |  | 80
R9, R10, R11, R22, R23, R24, R25, R26, R27, R28, R29, R30, R31, R32, R33, R34, R35, R36, | 18 | 1k | Resistor_0805 | Resistor_SMD:R_0805_2012Metric_Pad1.20x1.40mm_HandSolder | Resistor | farnell | 1440 | 1520 | 31258 |  | y | y | y | 80 | 2332071 | https://uk.farnell.com/te-connectivity/crgh0805f1k0/res-1k-1-0-33w-0805-thick-film/dp/2332071?st=1k%200805 |  | 80
R12, R13, | 2 | 470r | Resistor_0805 | Resistor_SMD:R_0805_2012Metric_Pad1.20x1.40mm_HandSolder | Resistor | farnell | 160 | 170 | 31258 |  | y | y | y | 10 | 2670094 | https://uk.farnell.com/walsin/wf08p4700ftl/res-470r-1-0-25w-0805-thick-film/dp/2670094?st=470r%200805 |  | 80
R15, R16, R18, R20, | 4 | 10k | Resistor_0805 | Resistor_SMD:R_0805_2012Metric_Pad1.20x1.40mm_HandSolder | Resistor | farnell | 320 | 500 | 31258 |  | y | y | y | 180 | 2447553RL | https://uk.farnell.com/multicomp/mcwr08x1002ftl/res-10k-1-0-125w-0805-thick-film/dp/2447553RL?st=10k%200805 |  | 80
R17, R19, R21, | 3 | 2k7 | Resistor_0805 | Resistor_SMD:R_0805_2012Metric_Pad1.20x1.40mm_HandSolder | Resistor | farnell | 240 | 260 | 31258 |  | y | y | y | 20 | 2447627 | https://uk.farnell.com/multicomp/mcwr08x2701ftl/res-2k7-1-0-125w-thick-film/dp/2447627?st=2k7%200805 |  | 80
SW1, | 1 | Stepper_Mode | SW_DIP_x03 | Button_Switch_SMD:SW_DIP_SPSTx03_Slide_6.7x9.18mm_W6.73mm_P2.54mm_LowProfile_JPin | 3x DIP Switch, Single Pole Single Throw (SPST) switch, small symbol | farnell | 80 | 90 | 31258 |  | y | n | 2022-09-15 | 10 | 3778050 | https://uk.farnell.com/cts/219-3lpstr/dip-switch-0-1a-50vdc-3pos-smd/dp/3778050?st=dipswitches |  | 80
SW2, SW3, | 2 | Student Reset | pushbutton_tactile_2pin_SMD |  | MEC 5E single pole normally-open tactile switch | farnell | 160 | 170 | 31258 |  | y | y | y | 10 | 2320087RL | https://uk.farnell.com/c-k-components/pts645sm43smtr92lfs/switch-spst-0-05a-12vdc-smd-4/dp/2320087RL |  | 80
 |  |  |  |  |  |  | 0 |  |  |  |  |  |  | 0 |  |  |  | 80
U3, | 1 | AMS1117-3.3 | AMS1117-3.3 | Package_TO_SOT_SMD:SOT-223-3_TabPin2 | 1A Low Dropout regulator, positive, 3.3V fixed output, SOT-223 | farnell | 80 | 100 | 31258 |  | y | y | y | 20 | 1652366RL | https://uk.farnell.com/on-semiconductor/ncp1117st33t3g/ic-linear-voltage-regulator/dp/1652366RL?st=ldo |  | 80
U4, U6, | 2 | ATSAMD21G18A-M | ATSAMD21G18A-M | Package_DFN_QFN:QFN-48-1EP_7x7mm_P0.5mm_EP5.15x5.15mm | SAM D21 Microchip SMART ARM-based Flash MCU, 48Mhz, 256K Flash, 32K SRAM, QFN-48 |  | 160 | 0 | not req |  | n | n | NOT REQUIRED |  |  |  |  | 80
U5, U7, | 2 | 4094 | 4094 | Package_DIP:SMDIP-18_W9.53mm | 8-bit serial in/out Shift Register 3-State Outputs | farnell | 160 | 170 | 31258 |  | y | y | y | 10 | 1201297 | https://uk.farnell.com/nexperia/hef4094bt/ic-4000-locmos-smd-4094-soic16/dp/1201297?st=4094 | https://www.mouser.co.uk/ProductDetail/Nexperia/HEF4094BT653?qs=me8TqzrmIYXYasToWufdKw%3D%3D | 80
U8, | 1 | 4069 | 4069 | Package_DIP:SMDIP-14_W9.53mm | Hex inverter | farnell | 80 | 100 | 31258 |  | y | y | y | 20 | 1201295 | https://uk.farnell.com/nexperia/hef4069ubt/ic-4000-locmos-smd-4069-soic14/dp/1201295?st=4069 |  | 80
U9, U10, U11, U12, | 4 | 4081 | 4081 | Package_DIP:SMDIP-14_W9.53mm | Quad And 2 inputs | farnell | 320 | 340 | 31258 |  | y | y | y | 20 | 1085290 | https://uk.farnell.com/nexperia/hef4081bt/ic-4000-locmos-smd-4081-soic14/dp/1085290?st=4081 |  | 80
U13, U14, | 2 | 74HC86 | 74HC86 | Package_DIP:SMDIP-14_W9.53mm | Quad 2-input XOR | farnell | 160 | 170 | 31258 |  | y | y | y | 10 | 1085331 | https://uk.farnell.com/nexperia/74hc86d/ic-74hc-cmos-smd-74hc86-soic14/dp/1085331?st=74hc86 |  | 80
U15, U16, U17, | 3 | NCS20074D | NCS20074D | Package_SO:SOIC-14_3.9x8.7mm_P1.27mm | Quad, 2.8V/Ã‚Âµs, Rail-to-Rail Output, SOIC-14 | farnell | 240 | 252 | 31258 |  | y | y | y | 12 | 2774608 | https://uk.farnell.com/on-semiconductor/ncs20074dr2g/op-amp-quad-3mhz-2-8v-us-soic/dp/2774608?st=ncs20074 |  | 80
U1, U18, | 2 | R-78C5.0-1.0 | R-78C5.0-1.0 | Converter_DCDC:Converter_DCDC_RECOM_R-78E-0.5_THT | 1A Step-Down DC/DC-Regulator, 7-42V input, 5V fixed Output Voltage, LM78xx replacement, -40Ã‚Â°C to +85Ã‚Â°C, SIP3 | RS Online | 160 | 84 | 31361 |  | y | y | y | -76 | 193-4004 | https://uk.rs-online.com/web/p/switching-regulators/1934004 |  | 80
U19, | 1 | AD8497 | AD8497 | Package_SO:MSOP-8_3x3mm_P0.65mm | Precision Thermocouple Amplifiers with Cold Junction Compensation, K-Type Thermocouple, 25 to 100C, MSOP-8 |  | 80 | 0 |  |  | n | n | NOT AVAILABLE |  |  |  |  | 80
U20, U21, U22, | 3 | 74LS07 | 74LS07 | SOIC-14 | Hex Buffers and Drivers With Open Collector High Voltage Outputs | RS Online | 240 | 250 | 31244 |  | y | y | y | 10 | 827-0301 | https://uk.rs-online.com/web/p/buffers/8270301 |  | 80
Y1, Y2, | 2 | 32.768 kHz | Crystal_Small | Crystal:Crystal_SMD_SeikoEpson_MC405-2Pin_9.6x4.1mm_HandSoldering | Two pin crystal, small symbol | farnell | 160 | 170 | 31258 |  | y | y | y | 10 | 2467903 | https://uk.farnell.com/abracon/asek-32-768khz-lrt/osc-32-768khz-3-2-x-2-5mm-lvcmos/dp/2467903 |  | 80
 |  |  |  |  |  |  | 0 |  |  |  |  |  |  | 0 |  |  |  | 80
 |  |  |  |  |  |  | 0 |  |  |  |  |  |  |  |  |  |  | 80
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

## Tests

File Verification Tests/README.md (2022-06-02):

# Remote Labs Supervisor PCB Verification Firmware

_This folder contains a range of firmware options to enable verification testing of all the functions of the Supervisor PCB._ <br>

As there is a few different ways the PCB can be populated, for the time being all pin references are assuming that the board will be used with Arduino Nano IoT 33 as the MCU, and shift registers
are installed to expand the number of IO pins.

## Pin Declarations

_Pin Declarations, references and Functions can be found in the Excel Spreadsheet Supervisor_PCB_PinMap_

This is used to generate 2 header files:

supervisor_pinMap.h
student_pinMap.h

which will list all IO pins referencing their arduino pin numbers with the PCB pin name. 

## Functions to Test

### Sensor Inputs

[x] if included in program

- Optical Encoder															 	[x]
- Limit Switches (1 )															[x]
- Thermocouple [Unavailable due to component supply]							[ ]
- Motor Driver Current 1														[X]
- Motor Driver Current 2														[X]
- Stepper Motor Fault Detect													[X]
- Student to Supervisor Servo Detection											[x]

_All sensor inputs are mirrored over each MCU, therefore the same software written to test the data aquisition can be programmed into both MCUs and measurements compared._

_Note: There will be some discrepancy between readings due to additional Current Limiting Resistors between the AI pins of the student MCU and the signal distribution amplifyers/buffers. 
the difference between the two ADC Readings can be used as a small focus for experimentation_

For Motor Driver Current 1 and 2, Motor speed will be controlled via supervisor, while current readings are taken on both MCUs

For Optical Encoder testing, motor will be unpowered and the encoder manipulated by hand.

#### Supervisor

#### Student

### Actuator Outputs
_Note: To fully test the actuator outputs, supervisor MCU must enable outputs for student MCU_

#### Supervisor

- LED_BUILTIN  (Pin D13 - SCK) 													[x]
- DC Motor																		[x]	
- Stepper Motor																	[x]														
- Servo Motor																	[x]
- WS2812B LEDs																	[x]

#### Student

- LED_BUILTIN   (Pin D13 - SCK)                                                    [x]
- DC Motor																			[]
- Stepper Motor																		[]
- Servo Motor - Via analogRead on supervisor (Translate to output for test?)		[]
- WS2812B LEDs																		[]

#### Supervisor Output Control
_Test each enable pin seperatly to confirm control by student is blocked_

- Student DC Motor Enable														[x]
- Student Stepper Motor Enable													[x]
- Student Pixel Enable															[x]

- Student to Supervisor Servo 1													[]

## Power & Other PCB Functions
_Test that do not require MCUs to test function_

- 12v Bus Voltage
- 5V Power Bus Voltage
- 5v Raspi Bus Voltage
- USB power of MCUs [Requires cutting trace on PCB]
- 3v3 MCU Bus Voltage
- Power LEDs showing for 12v and for 3v3.
-

## Test Firmware Details

supervisorTest.ino

studentTest.ino

Each program contains all the functions to cross test all hardware, a config file can be generated for each test which will set each function for that test.

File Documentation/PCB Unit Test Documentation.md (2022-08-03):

# Remote Labs Supervisor PCB v1.0 Testing Documentation
*Author: Bhavith Manapoty
Created On: 26 June 2022
https://bhavithmanapoty.com*

## Hardware Changes and Tests:

### Modifications Made to Board:
1. Trace from U13 Pin 8 to Stepper Motor Driver Enable Pin (A4 Pin 1) was cut.
2. Trace from 3.3V to Optical Encoder was cut.
3. Optical Encoder power is now supplied from a 5V bus.
4. U13 Pin 8 is now connected to Stepper Motor Driver Sleep Pin (A4 Pin 6).
5. Pullup resistors were added to the buffers U20, U21, U22. New buffers which do not need pullup resistors have been ordered. Resistors have been added to Pins 2,4,6,8,10,12 of each buffer.

### Test 1: Smoke Test (Without Valuable Components)
Connect power supply to the PCB (with no valuable components connected) and check if smoke is released from any part of the board.

Expected Observations:
|Test      |Description                                           |Expected Observation|
|----------|------------------------------------------------------|--------------------|
|Smoke Test|Check if smoke is releases when power supply is connected|No smoke released   |

### Test 2: Check Voltages:
Connect power supply to the PCB and measure the voltages at the following points. Ensure not to connect any valuable components.
- J31 - 5V Pin
- J30 - 12V Pin
- A3 - VBAT
- J6 - 5V Pin
- J34 - 5V Bus
- J33 - 12V Bus
- J35 - 5V Bus
- J36 - 3.3V Bus
- A4 - Pin 16

Expected Observations:
|Pin|Expected Output|
|---|---------------|
|A3 - VBAT|~12V|
|A4 - Pin 16|~12V|
|J6 - 5V Pin|~5V|
|J30 - 12V Pin|~12V|
|J31 - 5V Pin|~5V|
|J33 - 12V Bus|~12V|
|J34 - 5V Bus|~5V|
|J35 - 5V Bus|~5V|
|J36 - 3.3V Bus|~3.3V|

### Test 3: Smoke Test (With Valuable Components)
Connect all valuable components to the PCB and then connect the power supply to the PCB. Check if smoke is released from any part of the board.

Expected Observations:
|Test      |Description                                           |Expected Observation|
|----------|------------------------------------------------------|--------------------|
|Smoke Test|Check if smoke is releases when power supply is connected|No smoke released   |

### Test 4: Check Voltages:
Repeat Test 2 after connecting all components to ensure the results are the same.

## Supervisor Software Tests: 

### Test 5: Supervisor Limit Switch Test:
Connect the Supervisor Arduino Nano 33 IoT to the PCB. Connect the Limit Switch to the PCB. Upload the code from [here](https://github.com/ImogenWren/RemoteLabs_Supervisor_PCB/blob/main/Verification%20Tests/PCB%20Unit%20Tests/Supervisor%20Tests/Limit%20Switch%20Test/supervisorTest/supervisorTest.ino).

Expected Observations:
|Test      |Description                                           |Expected Observation|
|----------|------------------------------------------------------|--------------------|
|Limit Switch Test|Press Limit Switch during runtime|Serial Print should read "Limit Switch Pressed"   |

### Test 6: Supervisor LED Test:
Connect the Supervisor Arduino Nano 33 IoT to the PCB. Connect the LED to the PCB. Upload the code from [here](https://github.com/ImogenWren/RemoteLabs_Supervisor_PCB/blob/main/Verification%20Tests/PCB%20Unit%20Tests/Supervisor%20Tests/LED%20Test/supervisorTest/supervisorTest.ino).

Expected Observations:
|Test      |Description                                           |Expected Observation|
|----------|------------------------------------------------------|--------------------|
|LED Test|LED Test|LED should switch on and change colors in a breathing pattern|

### Test 7: Supervisor Stepper Motor Test:
Connect the Supervisor Arduino Nano 33 IoT to the PCB. Connect the Stepper Motor to the PCB. Upload the code from [here](https://github.com/ImogenWren/RemoteLabs_Supervisor_PCB/blob/main/Verification%20Tests/PCB%20Unit%20Tests/Supervisor%20Tests/Stepper%20Test/supervisorTest/supervisorTest.ino).

Expected Observations:
|Test      |Description                                           |Expected Observation|
|----------|------------------------------------------------------|--------------------|
|Stepper Motor Test|Stepper Motor Test|Stepper motor should make two whole rotations in one direction, wait for 2 seconds, and then make two rotations in the other direction. This should keep repeating.|
**NOTE: The motor should only draw current when it is rotating and not when it is still. If there is current being drawn at all times, the motor will get extremely hot.**

### Test 8: Supervisor DC Motor Test:
Connect the Supervisor Arduino Nano 33 IoT to the PCB. Connect the DC Motor to the PCB. Upload the code from [here](https://github.com/ImogenWren/RemoteLabs_Supervisor_PCB/blob/main/Verification%20Tests/PCB%20Unit%20Tests/Supervisor%20Tests/Motor%20Test/supervisorTest/supervisorTest.ino).

Expected Observations:
|Test      |Description                                           |Expected Observation|
|----------|------------------------------------------------------|--------------------|
|DC Motor Test|DC Motor Test|DC Motor should rotate in the given direction (from the code) at the given speed (from the code)|
Repeat this test changing the direction and motor speed in the code to verify that it works.

**NOTES:**
1. Do not increase speed over 100 as it is a very powerfull motor.
2. If the direction of rotation is incorrect from the code, the wires of the motor may be dconnected to the PCB in the wrong way. To fix this, intercahnge the orientation of the wires on the PCB.

## Supervisor and Student Software Tests:
### Test 9: Full Software LED Test:
This test checks if the student can control the LED. It also checks whether the supervisor can enable and disable control access for the student.
#### Supervisor Allowing Student to Control LED:
Connect both Arduino Nano 33 IoT boards to the PCB. Connect the LED to the PCB. 
Upload the code for the supervisor from [here](https://github.com/ImogenWren/RemoteLabs_Supervisor_PCB/blob/main/Verification%20Tests/PCB%20Unit%20Tests/LED%20Test/Supervisor%20Allowed/supervisorTest/supervisorTest.ino).
Upload the code for the student from [here](https://github.com/ImogenWren/RemoteLabs_Supervisor_PCB/blob/main/Verification%20Tests/PCB%20Unit%20Tests/LED%20Test/Supervisor%20Allowed/studentTest/studentTest.ino).

Expected Observations:
|Test      |Description                                           |Expected Observation|
|----------|------------------------------------------------------|--------------------|
|LED Test|LED Test|Student should be allowed to control LED. Hence LED should be switched on|
#### Supervisor NOT Allowing Student to Control LED:
Connect both Arduino Nano 33 IoT boards to the PCB. Connect the LED to the PCB. 
Upload the code for the supervisor from [here](https://github.com/ImogenWren/RemoteLabs_Supervisor_PCB/blob/main/Verification%20Tests/PCB%20Unit%20Tests/LED%20Test/Supervisor%20Not%20Allowed/supervisorTest/supervisorTest.ino).
Upload the code for the student from [here](https://github.com/ImogenWren/RemoteLabs_Supervisor_PCB/blob/main/Verification%20Tests/PCB%20Unit%20Tests/LED%20Test/Supervisor%20Not%20Allowed/studentTest/studentTest.ino).

Expected Observations:
|Test      |Description                                           |Expected Observation|
|----------|------------------------------------------------------|--------------------|
|LED Test|LED Test|Student should not be allowed to control LED. Hence LED should be switched off|

**Final Test Observations:**
|Test      |Description                                           |Expected Observation|
|----------|------------------------------------------------------|--------------------|
|Supervisor and Student LED Test|Supervisor and Student LED Test|Supervisor should be able to enable and diable LED control access to the student|

### Test 10: Full Software DC Motor Test:
This test checks if the student can control the DC Motor. It also checks whether the supervisor can enable and disable control access for the student.
#### Supervisor Allowing Student to Control Motor:
Connect both Arduino Nano 33 IoT boards to the PCB. Connect the DC Motor to the PCB. 
Upload the code for the supervisor from [here](https://github.com/ImogenWren/RemoteLabs_Supervisor_PCB/blob/main/Verification%20Tests/PCB%20Unit%20Tests/Motor%20Test/Supervisor%20Allowed/supervisorTest/supervisorTest.ino).
Upload the code for the student from [here](https://github.com/ImogenWren/RemoteLabs_Supervisor_PCB/blob/main/Verification%20Tests/PCB%20Unit%20Tests/Motor%20Test/Supervisor%20Allowed/studentTest/studentTest.ino).

Expected Observations:
|Test      |Description                                           |Expected Observation|
|----------|------------------------------------------------------|--------------------|
|Motor Test|Motor Test|Student should be allowed to control motor. Hence the motor should be rotating in the given direction and given speed in the Student Code|
#### Supervisor NOT Allowing Student to Control Motor:
Connect both Arduino Nano 33 IoT boards to the PCB. Connect the Motor to the PCB. 
Upload the code for the supervisor from [here](https://github.com/ImogenWren/RemoteLabs_Supervisor_PCB/blob/main/Verification%20Tests/PCB%20Unit%20Tests/Motor%20Test/Supervisor%20Not%20Allowed/supervisorTest/supervisorTest.ino).
Upload the code for the student from [here](https://github.com/ImogenWren/RemoteLabs_Supervisor_PCB/blob/main/Verification%20Tests/PCB%20Unit%20Tests/Motor%20Test/Supervisor%20Not%20Allowed/studentTest/studentTest.ino).

Expected Observations:
|Test      |Description                                           |Expected Observation|
|----------|------------------------------------------------------|--------------------|
|Motor Test|Motor Test|Student should not be allowed to control motor. Hence the motor should be switched off|

**Final Test Observations:**
|Test      |Description                                           |Expected Observation|
|----------|------------------------------------------------------|--------------------|
|Supervisor and Student Motor Test|Supervisor and Student Motor Test|Supervisor should be able to enable and diable motor control access to the student|

### Test 11: Full Software Stepper Motor Test:
This test checks if the student can control the Stepper Motor. It also checks whether the supervisor can enable and disable control access for the student.
#### Supervisor Allowing Student to Control Stepper Motor:
Connect both Arduino Nano 33 IoT boards to the PCB. Connect the Stepper Motor to the PCB. 
Upload the code for the supervisor from [here](https://github.com/ImogenWren/RemoteLabs_Supervisor_PCB/blob/main/Verification%20Tests/PCB%20Unit%20Tests/Stepper%20Test/Supervisor%20Allowed/supervisorTest/supervisorTest.ino).
Upload the code for the student from [here](https://github.com/ImogenWren/RemoteLabs_Supervisor_PCB/blob/main/Verification%20Tests/PCB%20Unit%20Tests/Stepper%20Test/Supervisor%20Allowed/studentTest/studentTest.ino).

Expected Observations:
|Test      |Description                                           |Expected Observation|
|----------|------------------------------------------------------|--------------------|
|Stepper Motor Test|Stepper Motor Test|Student should be allowed to control stepper motor. Hence the stepper should be rotating in the given direction for the given number of rotations in the Student Code|
**NOTE: The motor should only draw current when it is rotating and not when it is still. If there is current being drawn at all times, the motor will get extremely hot.**
#### Supervisor NOT Allowing Student to Control Stepper Motor:
Connect both Arduino Nano 33 IoT boards to the PCB. Connect the Stepper Motor to the PCB. 
Upload the code for the supervisor from [here](https://github.com/ImogenWren/RemoteLabs_Supervisor_PCB/blob/main/Verification%20Tests/PCB%20Unit%20Tests/Stepper%20Test/Supervisor%20Not%20Allowed/supervisorTest/supervisorTest.ino).
Upload the code for the student from [here](https://github.com/ImogenWren/RemoteLabs_Supervisor_PCB/blob/main/Verification%20Tests/PCB%20Unit%20Tests/Stepper%20Test/Supervisor%20Not%20Allowed/studentTest/studentTest.ino).

Expected Observations:
|Test      |Description                                           |Expected Observation|
|----------|------------------------------------------------------|--------------------|
|Stepper Motor Test|Stepper Motor Test|Student should not be allowed to control Stepper Motor. Hence the stepper should be switched off|
**NOTE: The motor should only draw current when it is rotating and not when it is still. If there is current being drawn at all times, the motor will get extremely hot.**

**Final Test Observations:**
|Test      |Description                                           |Expected Observation|
|----------|------------------------------------------------------|--------------------|
|Supervisor and Student Stepper Motor Test|Supervisor and Student Stepper Motor Test|Supervisor should be able to enable and diable stepper motor control access to the student|

### Test 12: Full Software Servo Test:
This test checks if the student can control the Servo. It also checks whether the supervisor can enable and disable control access for the student.
#### Supervisor Allowing Student to Control Servo:
Connect both Arduino Nano 33 IoT boards to the PCB. Connect the Servo to the PCB. 
Upload the code for the supervisor from [here](https://github.com/ImogenWren/RemoteLabs_Supervisor_PCB/blob/main/Verification%20Tests/PCB%20Unit%20Tests/Servo%20Test/Supervisor%20Allowed/supervisorTest/supervisorTest.ino).
Upload the code for the student from [here](https://github.com/ImogenWren/RemoteLabs_Supervisor_PCB/blob/main/Verification%20Tests/PCB%20Unit%20Tests/Servo%20Test/Supervisor%20Allowed/studentTest/studentTest.ino).

Expected Observations:
|Test      |Description                                           |Expected Observation|
|----------|------------------------------------------------------|--------------------|
|Servo Test|Servo Test|**NEEDS TO BE WRITTEN**|

#### Supervisor NOT Allowing Student to Control Servo:
Connect both Arduino Nano 33 IoT boards to the PCB. Connect the Servo to the PCB. 
Upload the code for the supervisor from [here](https://github.com/ImogenWren/RemoteLabs_Supervisor_PCB/blob/main/Verification%20Tests/PCB%20Unit%20Tests/Servo%20Test/Supervisor%20Not%20Allowed/supervisorTest/supervisorTest.ino).
Upload the code for the student from [here](https://github.com/ImogenWren/RemoteLabs_Supervisor_PCB/blob/main/Verification%20Tests/PCB%20Unit%20Tests/Servo%20Test/Supervisor%20Not%20Allowed/studentTest/studentTest.ino).

Expected Observations:
|Test      |Description                                           |Expected Observation|
|----------|------------------------------------------------------|--------------------|
|Servo Test|Servo Test|**NEEDS TO BE WRITTEN**|

**Final Test Observations:**
|Test      |Description                                           |Expected Observation|
|----------|------------------------------------------------------|--------------------|
|Servo Test|Servo Test|**NEEDS TO BE WRITTEN**|

## Final Software Tests
### Test 13: Test all Software with All Components Plugged In
Repeat all Supervisor and Student software tests with all components plugged in. All tests should result in the same observations.

## Tests Pass/Fail:
**NOTE: For the Pass/Fail badges, use one of the following:**
https://img.shields.io/badge/Tests-PASS-success
https://img.shields.io/badge/Tests-FAIL-red
https://img.shields.io/badge/Tests-TESTING-lightgrey

|Test|Pass/Fail|
|----|---------|
|Test 1||
|Test 2||
|Test 3||
|Test 4||
|Test 5||
|Test 6||
|Test 7||
|Test 8||
|Test 9||
|Test 10||
|Test 11||
|Test 12||
|Test 13||

## Errors and Bugs Recorded:
1. While uploading code to the Arduino Boards, sometimes the DC Motor spins at full speed. This is potentially due to a PWM Signal being given to the motor pins during upload.
2. While uploading code to the Arduino Boards, sometimes the Stepper Motor rotates for 1 microstep in each direction continuously. This is potentially due to a PWM Signal being given to the stepper pins during upload.
3. While testing the DC Motor, the student is unable to control direction as the Supervisor is unable to perform a digitalRead on Analog Pins A0 and A1. These pins always read LOW even when the voltage on the pins is HIGH. This potentially due to an AnalogRead being called on those pins at some point in the code which causes the digitalRead values to be overwritten (This anamoly is tested and could potentially be the reason for the bug)

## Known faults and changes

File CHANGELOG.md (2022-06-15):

# PCB Design Changelog

### Changes from V1.0 to V1.1

- Optical Encoder power out changed from 3v3 to 5v rpi bus

 - Increase size of stepper motor driver PCB holes from 0.7mm to 1mm
 - Reduced distance between stepper motor driver pins by 1.27mm 

- Increased size of holes for DC/DC Buck converter from 0.7mm to 1mm

- Removed component values from PCB Silkscreen
- Increased text size for component references.

- Changed orientation of Optical Encoder connector as Vcc and GND were reversed

 - Increase CLR for 12v bus LED - DONE NOW 10k

- Changed STEPP_EN enable pin from both MCUs to SLP pin on stepper controller

- Changed SHIFT Reg Q7 output to STEPP_EN for Supervisor MCU. No Control for Student MCU 
- doesnt seem to change anything but at least its there incase

- Tied pull down resistors on stepper MODE inputs to VCC to pull up - standard mode is now finest resolution
- Tied Mode switches to GND to pull down when actuated.

#TODO:

- Add STEPP_SLP To Q7 shift register - How can this be coordinated between 2 MCUs?
 - NOTE ON ABOVE.
  CHANGING ENABLE PIN TO OPEN 
  SLEEP PIN NOW CONTROLLED INSTEAD OF ENABLE
- Stepper motor output make match evisting connectors?

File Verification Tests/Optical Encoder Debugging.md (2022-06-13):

Optical Encoder debugging

tested:
Optical Encodder [x]
pullup resistos [x]
software function [x]

to test
Physical Connection
Pin Defintion in software
buffers
power to buffers[]

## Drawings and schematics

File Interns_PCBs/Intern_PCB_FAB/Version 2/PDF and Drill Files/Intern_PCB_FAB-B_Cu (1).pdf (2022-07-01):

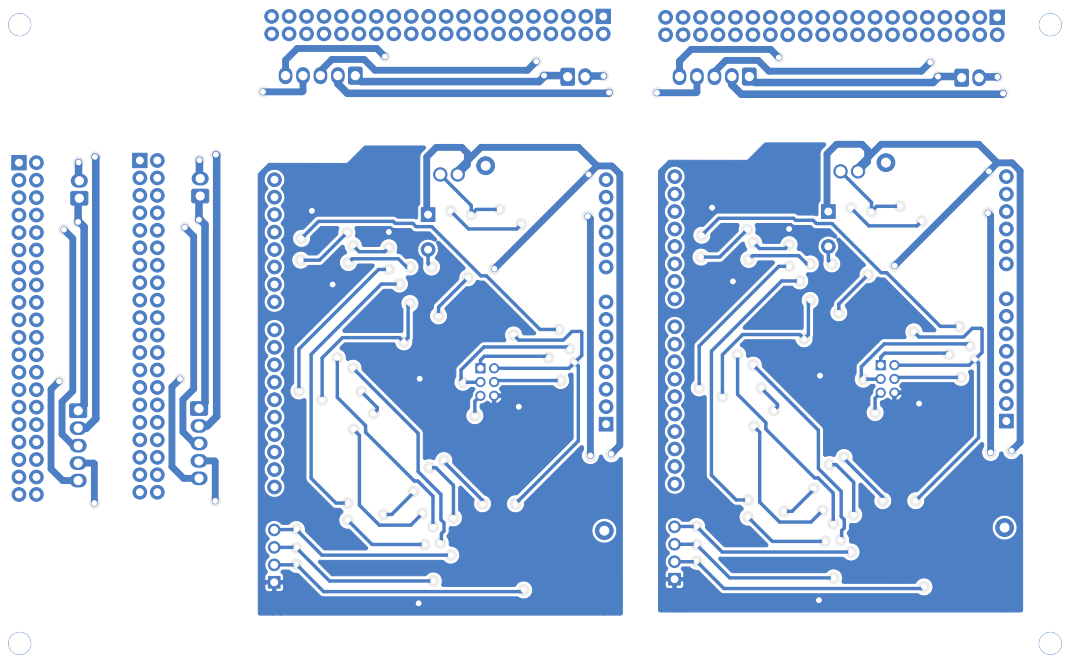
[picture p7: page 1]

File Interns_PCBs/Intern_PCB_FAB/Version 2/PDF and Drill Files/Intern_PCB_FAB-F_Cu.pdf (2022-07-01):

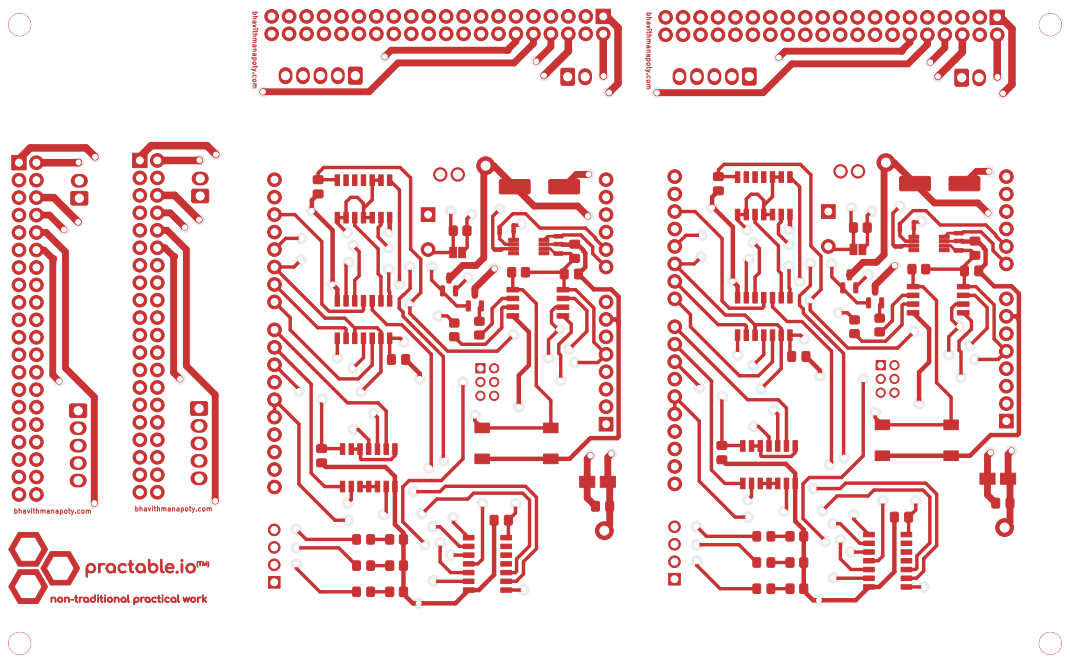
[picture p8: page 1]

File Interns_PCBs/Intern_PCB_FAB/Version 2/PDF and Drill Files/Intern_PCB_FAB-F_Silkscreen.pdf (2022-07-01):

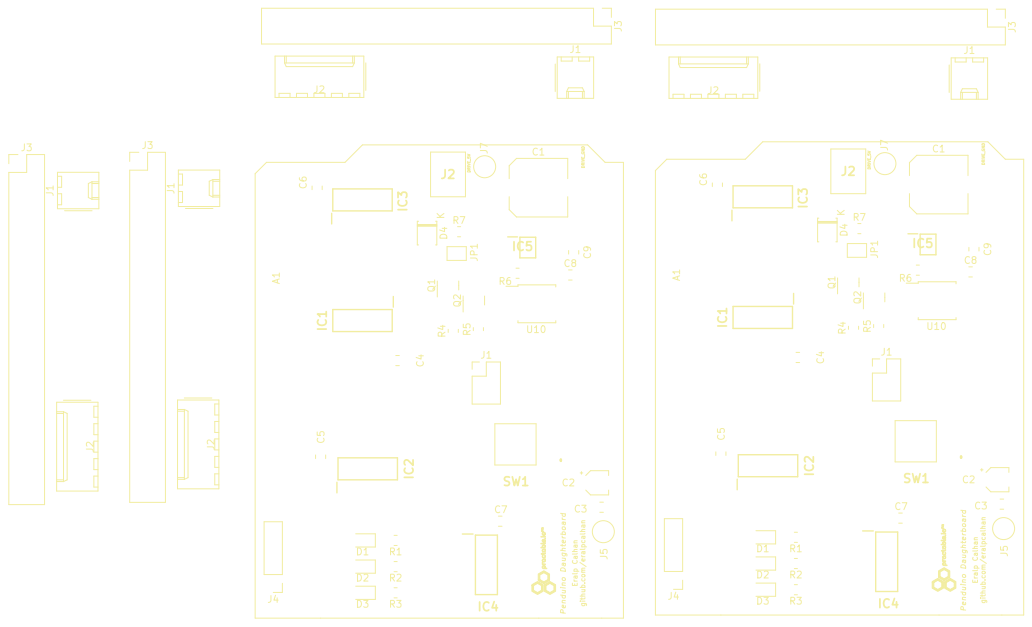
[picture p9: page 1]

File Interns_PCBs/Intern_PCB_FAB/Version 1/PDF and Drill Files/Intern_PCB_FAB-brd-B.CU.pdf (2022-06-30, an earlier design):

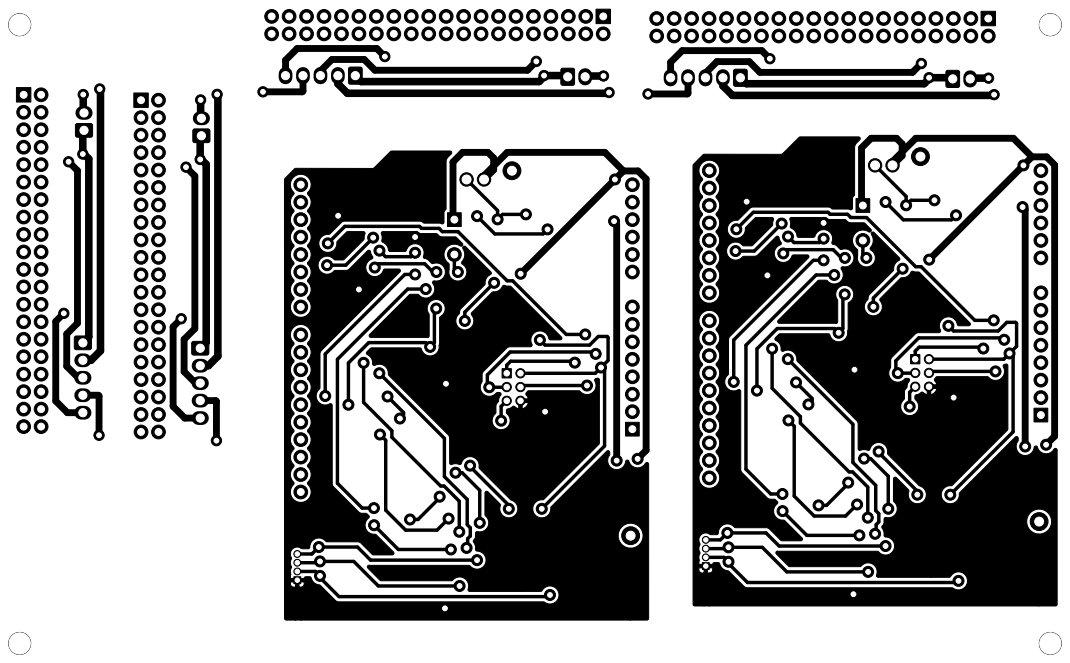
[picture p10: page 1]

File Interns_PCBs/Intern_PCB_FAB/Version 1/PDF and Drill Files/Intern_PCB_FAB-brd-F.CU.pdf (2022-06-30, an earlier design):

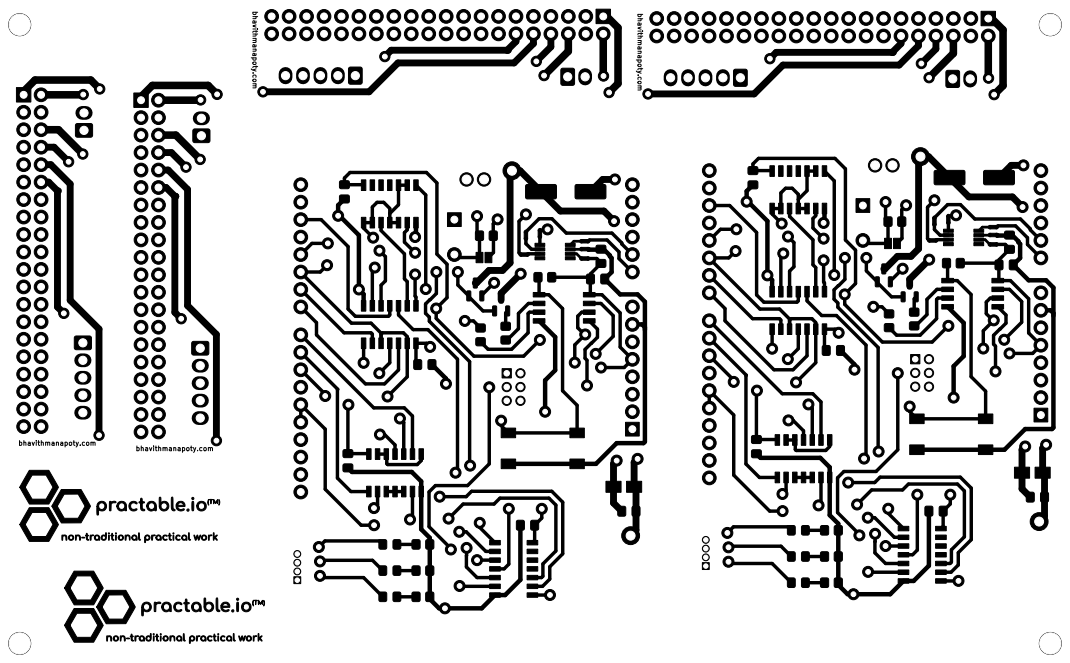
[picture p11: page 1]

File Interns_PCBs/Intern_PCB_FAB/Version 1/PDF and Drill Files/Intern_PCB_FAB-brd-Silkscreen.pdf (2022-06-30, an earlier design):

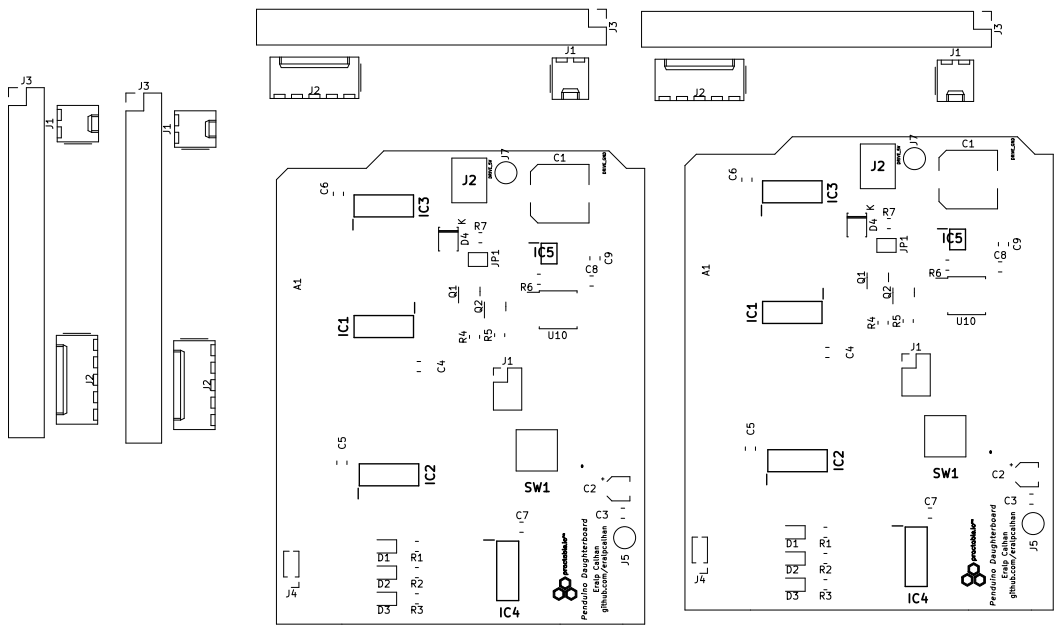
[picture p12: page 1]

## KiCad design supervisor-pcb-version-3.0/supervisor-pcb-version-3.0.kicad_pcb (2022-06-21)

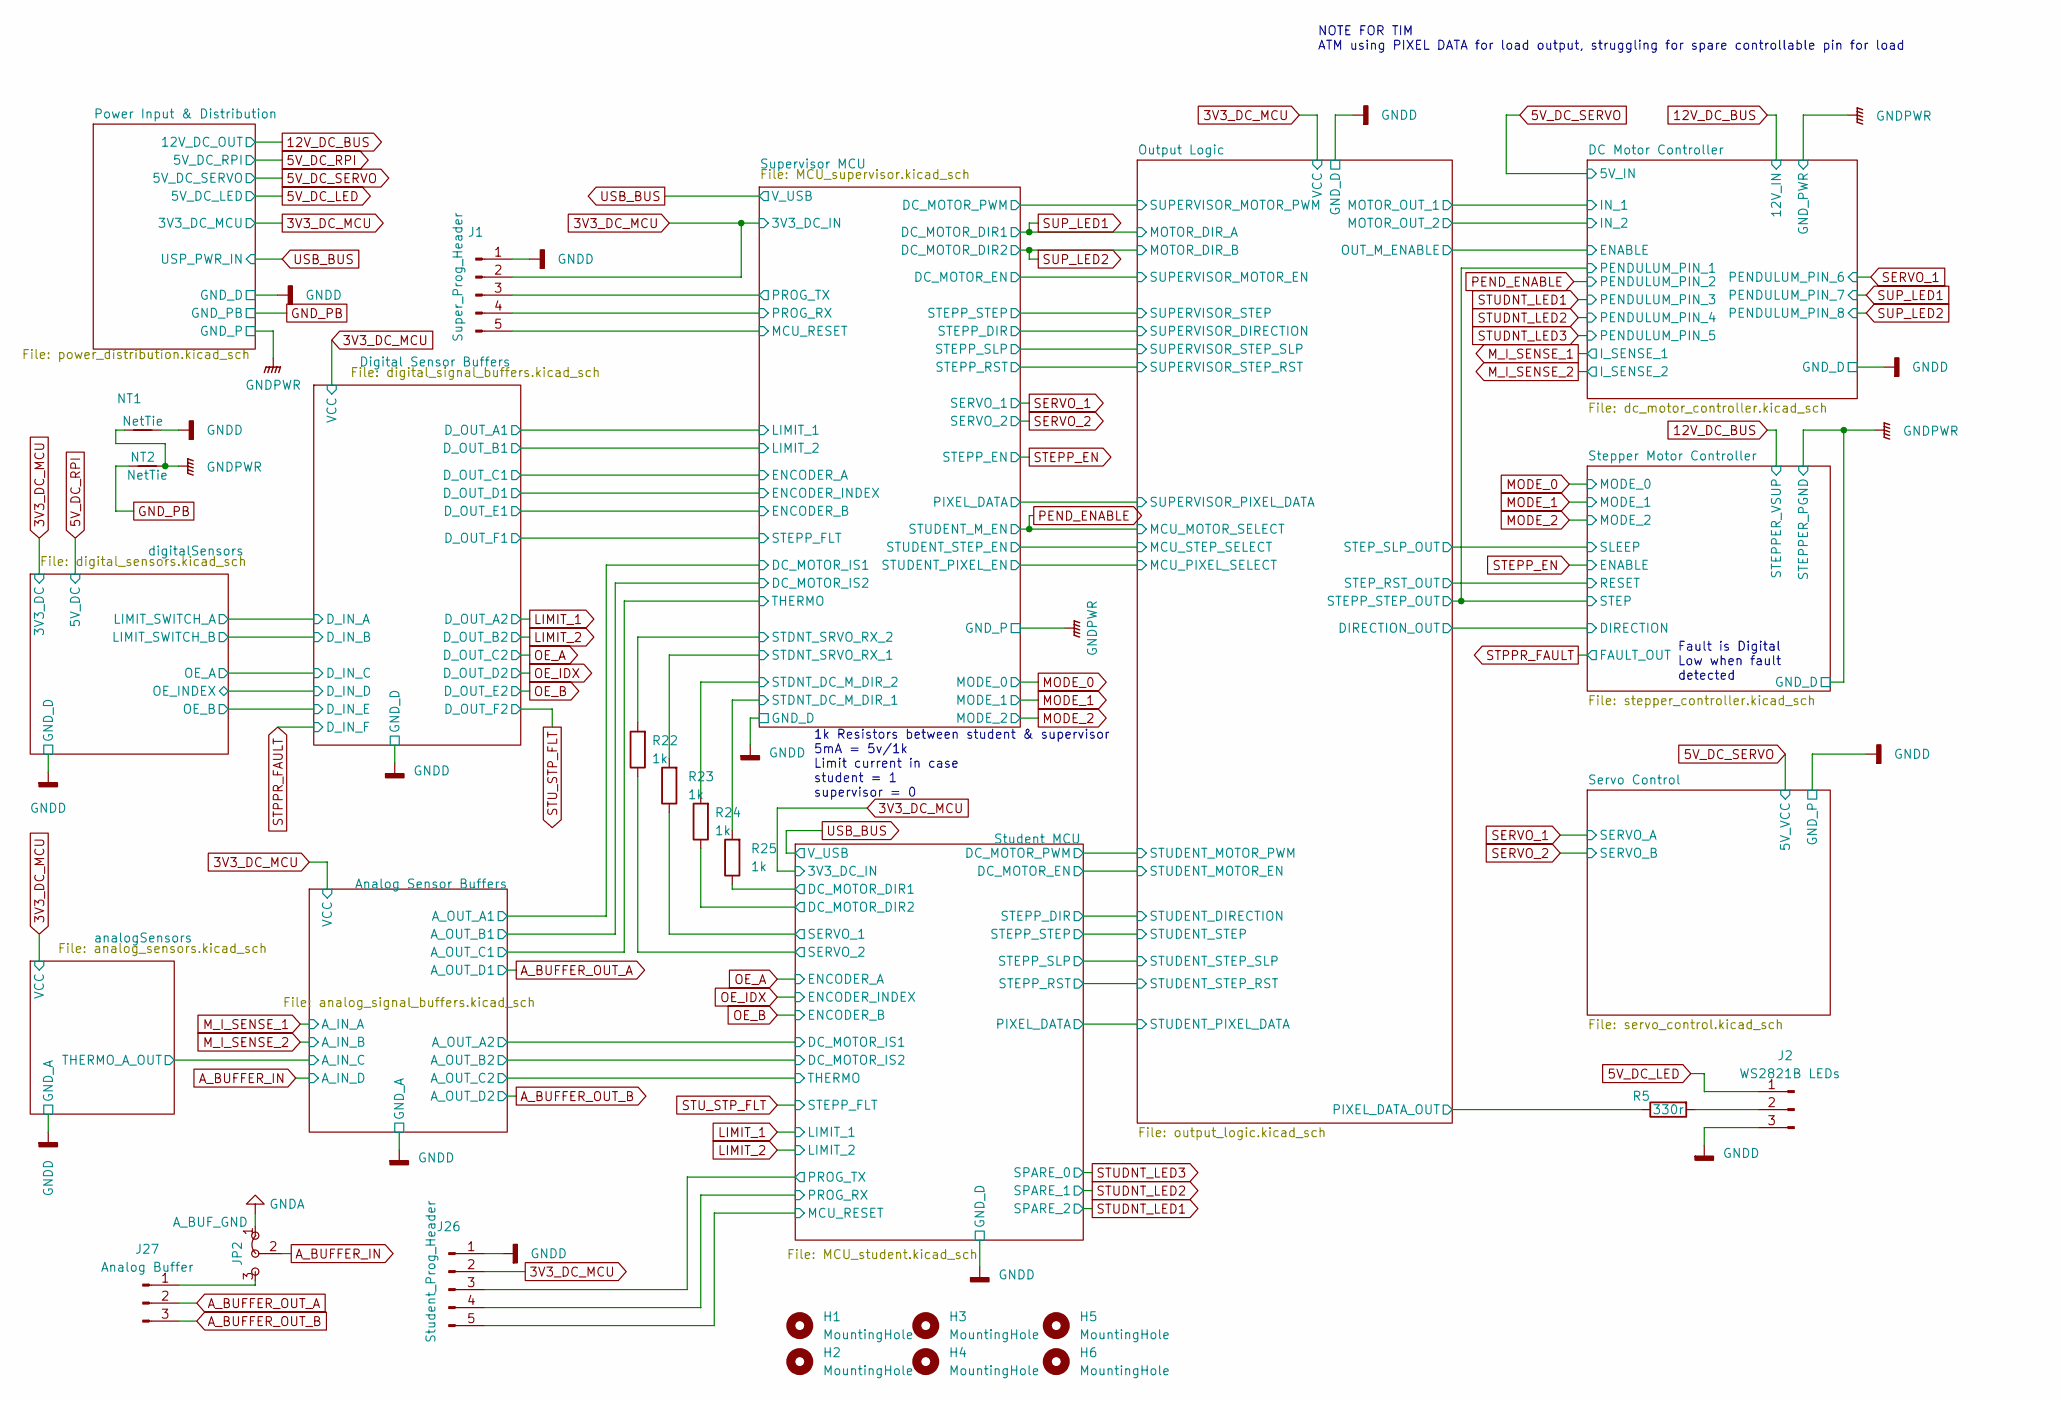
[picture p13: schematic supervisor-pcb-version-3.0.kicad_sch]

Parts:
H1, H2, H3, H4, H5, H6: MountingHole; MountingHole_3.2mm_M3_Pad_Via
J1: Super_Prog_Header; Molex_KK-254_AE-6410-05A_1x05_P2.54mm_Vertical
J2: WS2821B LEDs; Molex_KK-254_AE-6410-03A_1x03_P2.54mm_Vertical
J26: Student_Prog_Header; Molex_KK-254_AE-6410-05A_1x05_P2.54mm_Vertical
J27: Analog Buffer; PinHeader_1x03_P2.54mm_Vertical
JP2: A_BUF_GND; SolderJumper-3_P1.3mm_Bridged12_RoundedPad1.0x1.5mm
NT1: NetTie; NetTie-2_SMD_Pad2.0mm
NT2: NetTie; NetTie-2_SMD_Pad0.5mm
R5: 330r; R_0805_2012Metric_Pad1.20x1.40mm_HandSolder
R22, R23, R24, R25: 1k; R_0805_2012Metric_Pad1.20x1.40mm_HandSolder

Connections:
3V3_DC_MCU: J1.2, J26.2; also elsewhere on the board
5V_DC_LED: J2.1; also elsewhere on the board
/Output Logic/PIXEL_DATA_OUT: R5.1; also elsewhere on the board
/Student MCU/DC_MOTOR_DIR1: R25.1; also elsewhere on the board
/Student MCU/DC_MOTOR_DIR2: R24.1; also elsewhere on the board
/Student MCU/MCU_RESET: J26.5; also elsewhere on the board
/Student MCU/PROG_RX: J26.4; also elsewhere on the board
/Student MCU/PROG_TX: J26.3; also elsewhere on the board
/Student MCU/SERVO_1: R23.1; also elsewhere on the board
/Student MCU/SERVO_2: R22.1; also elsewhere on the board
/Supervisor MCU/MCU_RESET: J1.5; also elsewhere on the board
/Supervisor MCU/PROG_RX: J1.4; also elsewhere on the board
/Supervisor MCU/PROG_TX: J1.3; also elsewhere on the board
/Supervisor MCU/STDNT_DC_M_DIR_1: R25.2; also elsewhere on the board
/Supervisor MCU/STDNT_DC_M_DIR_2: R24.2; also elsewhere on the board
/Supervisor MCU/STDNT_SRVO_RX_1: R23.2; also elsewhere on the board
/Supervisor MCU/STDNT_SRVO_RX_2: R22.2; also elsewhere on the board
A_BUFFER_IN: JP2.2 (C); also elsewhere on the board
A_BUFFER_OUT_A: J27.2; also elsewhere on the board
A_BUFFER_OUT_B: J27.3; also elsewhere on the board
GNDA: JP2.1 (A)
GNDD: J1.1, J2.3, J26.1, NT1.1; also elsewhere on the board
GNDPWR: NT1.2, NT2.2; also elsewhere on the board
GND_PB: NT2.1; also elsewhere on the board
unnamed: J2.2, R5.2
unnamed: J27.1, JP2.3 (B)

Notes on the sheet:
1k Resistors between student & supervisor 5mA = 5v/1k Limit current in case student = 1 supervisor = 0
Fault is Digital Low when fault detected
NOTE FOR TIM ATM using PIXEL DATA for load output, struggling for spare controllable pin for load

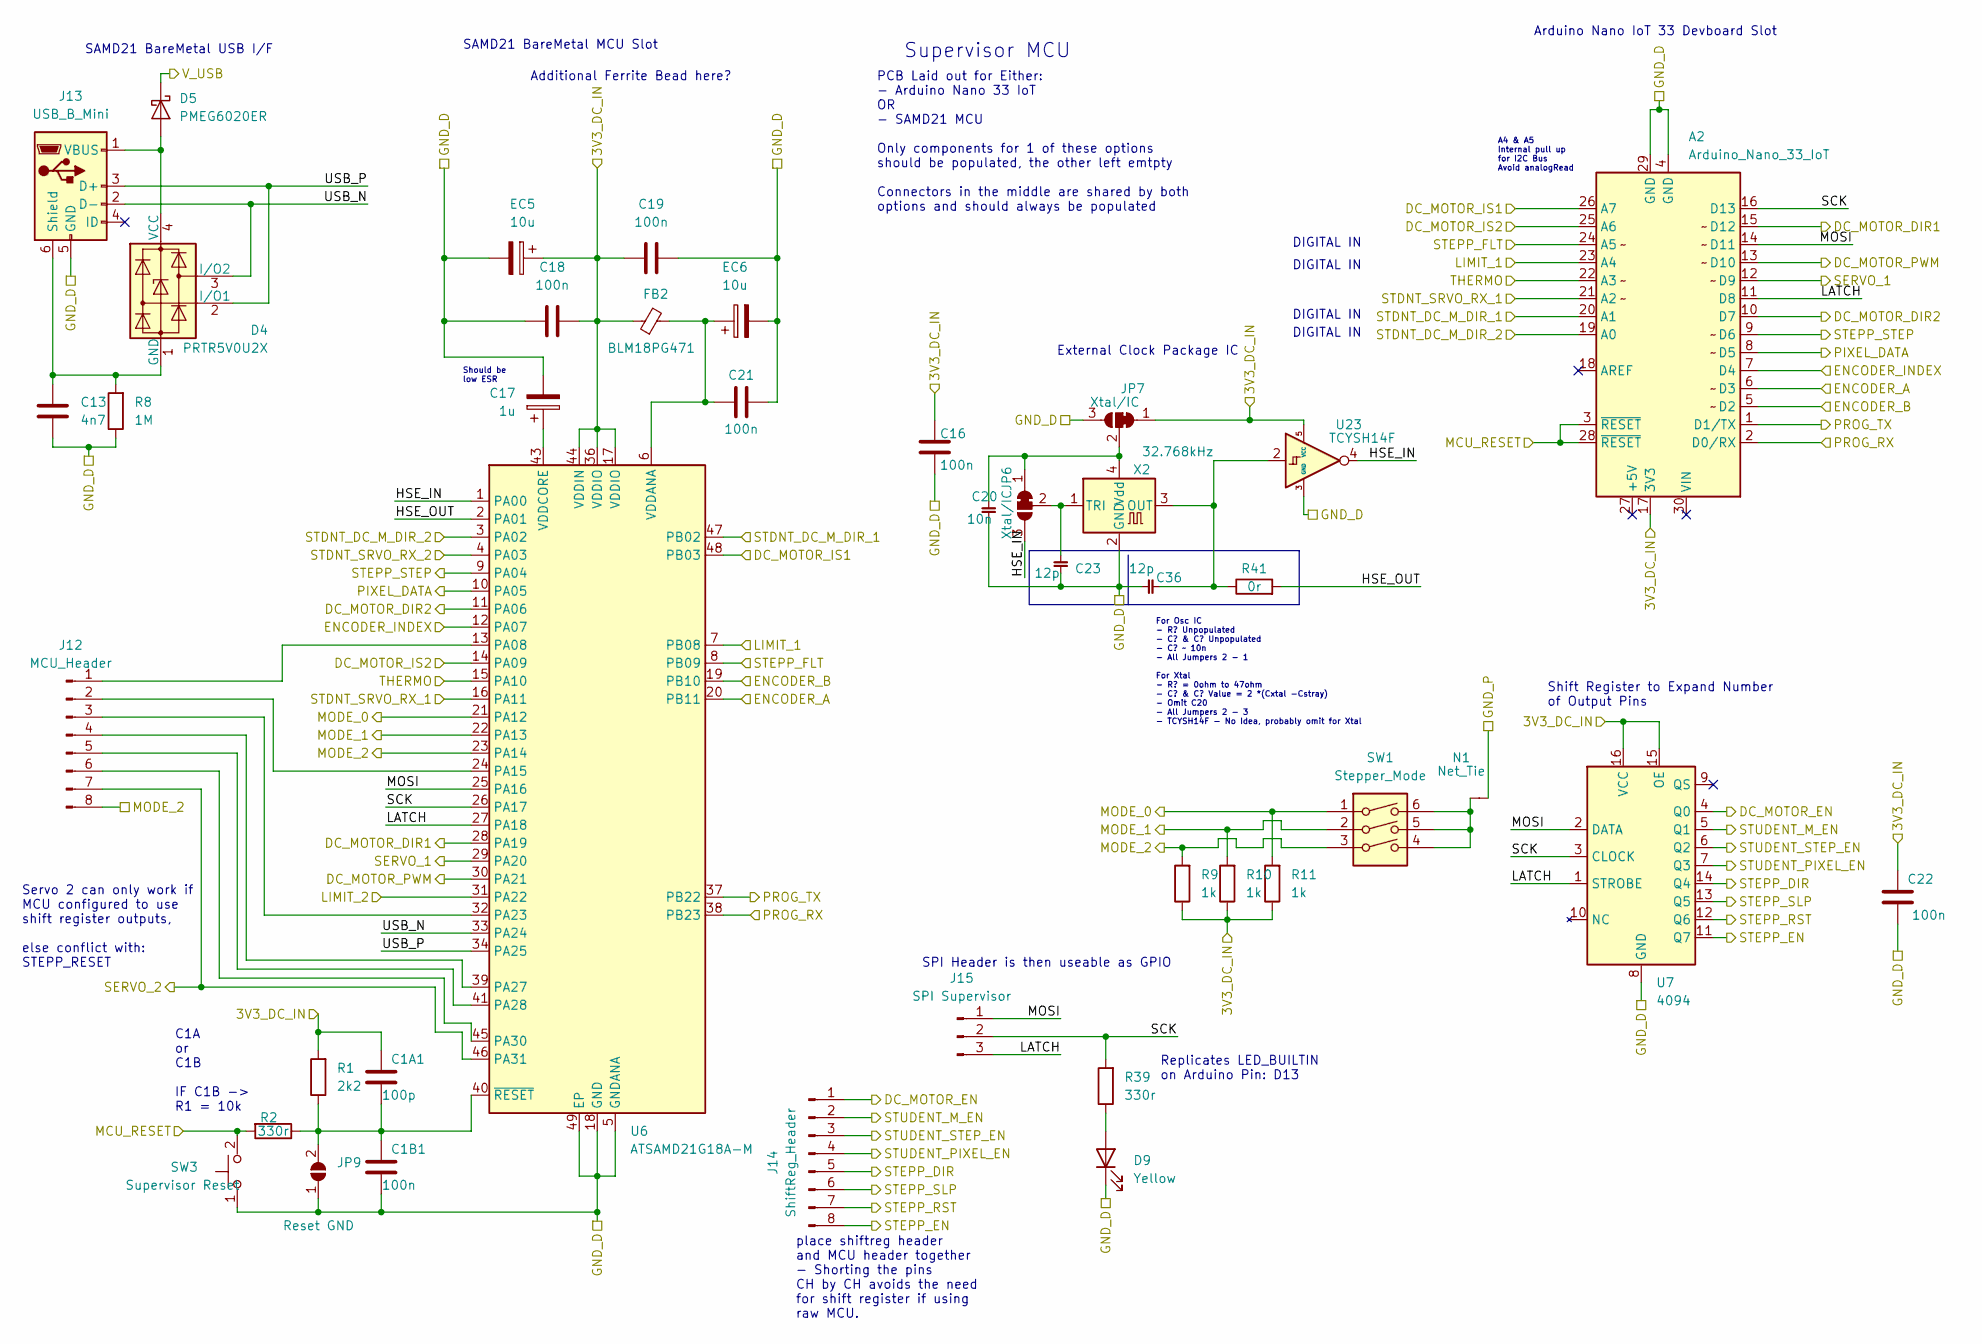
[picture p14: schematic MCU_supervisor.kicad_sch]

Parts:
A2: Arduino_Nano_33_IoT; Arduino_Nano
C1A1: 100p; C_0805_2012Metric_Pad1.18x1.45mm_HandSolder
C1B1, C16, C18, C19, C21, C22: 100n; C_0805_2012Metric_Pad1.18x1.45mm_HandSolder
C13: 4n7; C_0805_2012Metric_Pad1.18x1.45mm_HandSolder
C17: 1u; CP_EIA-2012-12_Kemet-R_Pad1.30x1.05mm_HandSolder
C20: 10n; C_0805_2012Metric_Pad1.18x1.45mm_HandSolder
C23, C36: 12p; C_0805_2012Metric_Pad1.18x1.45mm_HandSolder
D4: PRTR5V0U2X; SOT-143
D5: PMEG6020ER; Nexperia_CFP3_SOD-123W
D9: Yellow; D_0805_2012Metric_Pad1.15x1.40mm_HandSolder
EC5, EC6: 10u; CP_Elec_4x5.4
FB2: BLM18PG471; L_0805_2012Metric_Pad1.05x1.20mm_HandSolder
J12: MCU_Header; PinHeader_1x08_P2.54mm_Vertical
J13: USB_B_Mini; USB_Mini-B_Lumberg_2486_01_Horizontal
J14: ShiftReg_Header; PinHeader_1x08_P2.54mm_Vertical
J15: SPI Supervisor; PinHeader_1x03_P2.54mm_Vertical
JP6, JP7: Xtal/IC; SolderJumper-3_P1.3mm_Bridged12_RoundedPad1.0x1.5mm_NumberL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
JP9: Reset GND; SolderJumper-2_P1.3mm_Open_Pad1.0x1.5mm
N1: Net_Tie; NetTie-2_SMD_Pad0.5mm
R1: 2k2; R_0805_2012Metric_Pad1.20x1.40mm_HandSolder
R2, R39: 330r; R_0805_2012Metric_Pad1.20x1.40mm_HandSolder
R8: 1M; R_0805_2012Metric_Pad1.20x1.40mm_HandSolder
R9, R10, R11: 1k; R_0805_2012Metric_Pad1.20x1.40mm_HandSolder
R41: 0r; R_0805_2012Metric_Pad1.20x1.40mm_HandSolder
SW1: Stepper_Mode; SW_DIP_SPSTx03_Slide_6.7x9.18mm_W6.73mm_P2.54mm_LowProfile_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
SW3: Supervisor Reset; SW_Push_1P1T_NO_CK_KSC6xxJ
U6: ATSAMD21G18A-M; QFN-48-1EP_7x7mm_P0.5mm_EP5.15x5.15mm
U7: 4094; SOIC-16_3.9x9.9mm_P1.27mm
U23: TCYSH14F; SOT-23-5_HandSoldering
X2: 32.768kHz; Oscillator_SMD_Abracon_ASE-4Pin_3.2x2.5mm

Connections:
3V3_DC_MCU: A2.17 (3V3), C1A1.1, C16.1, C18.1, C19.2, C22.1, EC5.1, FB2.1, JP7.1 (A), R1.2, R9.1, R10.1, R11.1, U6.17 (VDDIO), U6.36 (VDDIO), U6.44 (VDDIN), U7.15 (OE), U7.16 (VCC), U23.5 (VCC); also elsewhere on the board
/Analog Sensor Buffers/A_OUT_A1: A2.26 (A7), U6.48 (PB03); also elsewhere on the board
/Analog Sensor Buffers/A_OUT_B1: A2.25 (A6), U6.14 (PA09); also elsewhere on the board
/Analog Sensor Buffers/A_OUT_C1: A2.22 (A3), U6.15 (PA10); also elsewhere on the board
/Digital Sensor Buffers/D_OUT_A1: A2.23 (A4), U6.7 (PB08); also elsewhere on the board
/Digital Sensor Buffers/D_OUT_B1: U6.31 (PA22); also elsewhere on the board
/Digital Sensor Buffers/D_OUT_C1: A2.6 (D3), U6.20 (PB11); also elsewhere on the board
/Digital Sensor Buffers/D_OUT_D1: A2.7 (D4), U6.12 (PA07); also elsewhere on the board
/Digital Sensor Buffers/D_OUT_E1: A2.5 (D2), U6.19 (PB10); also elsewhere on the board
/Digital Sensor Buffers/D_OUT_F1: A2.24 (A5), U6.8 (PB09); also elsewhere on the board
/Output Logic/MCU_PIXEL_SELECT: J14.4, U7.7 (Q3); also elsewhere on the board
/Output Logic/MCU_STEP_SELECT: J14.3, U7.6 (Q2); also elsewhere on the board
/Output Logic/SUPERVISOR_DIRECTION: J14.5, U7.14 (Q4); also elsewhere on the board
/Output Logic/SUPERVISOR_MOTOR_EN: J14.1, U7.4 (Q0); also elsewhere on the board
/Output Logic/SUPERVISOR_MOTOR_PWM: A2.13 (D10), U6.30 (PA21); also elsewhere on the board
/Output Logic/SUPERVISOR_PIXEL_DATA: A2.8 (D5), U6.10 (PA05); also elsewhere on the board
/Output Logic/SUPERVISOR_STEP: A2.9 (D6), U6.9 (PA04); also elsewhere on the board
/Output Logic/SUPERVISOR_STEP_RST: J14.7, U7.12 (Q6); also elsewhere on the board
/Output Logic/SUPERVISOR_STEP_SLP: J14.6, U7.13 (Q5); also elsewhere on the board
/Supervisor MCU/HSE_IN: JP6.3 (B), U6.1 (PA00), U23.4
/Supervisor MCU/HSE_OUT: R41.2, U6.2 (PA01)
/Supervisor MCU/LATCH: A2.11 (D8), J15.3, U6.27 (PA18), U7.1 (STROBE)
/Supervisor MCU/MCU_RESET: A2.3 (~RESET), A2.28 (~RESET), R2.2, SW3.2; also elsewhere on the board
/Supervisor MCU/MOSI: A2.14 (D11), J15.1, U6.25 (PA16), U7.2 (DATA)
/Supervisor MCU/PROG_RX: A2.2 (D0/RX), U6.38 (PB23); also elsewhere on the board
/Supervisor MCU/PROG_TX: A2.1 (D1/TX), U6.37 (PB22); also elsewhere on the board
/Supervisor MCU/SCK: A2.16 (D13), J15.2, R39.2, U6.26 (PA17), U7.3 (CLOCK)
/Supervisor MCU/STDNT_DC_M_DIR_1: A2.20 (A1), U6.47 (PB02); also elsewhere on the board
/Supervisor MCU/STDNT_DC_M_DIR_2: A2.19 (A0), U6.3 (PA02); also elsewhere on the board
/Supervisor MCU/STDNT_SRVO_RX_1: A2.21 (A2), U6.16 (PA11); also elsewhere on the board
/Supervisor MCU/STDNT_SRVO_RX_2: U6.4 (PA03); also elsewhere on the board
/Supervisor MCU/USB_N: D4.3 (I/O2), J13.2 (D-), U6.33 (PA24)
/Supervisor MCU/USB_P: D4.2 (I/O1), J13.3 (D+), U6.34 (PA25)
GNDD: A2.4 (GND), A2.29 (GND), C1B1.2, C13.2, C16.2, C17.2, C18.2, C19.1, C20.2, C21.1, C22.2, C23.2, C36.2, D9.1 (K), EC5.2, EC6.2, J13.5 (GND), JP7.3 (B), JP9.1 (A), R8.1, SW3.1, U6.5 (GNDANA), U6.18 (GND), U6.35 (GND), U6.42 (GND), U6.49 (EP), U7.8 (GND), U23.3 (GND), X2.2 (GND); also elsewhere on the board
GNDPWR: N1.2 (C); also elsewhere on the board
MODE_0: R11.2, SW1.1, U6.21 (PA12); also elsewhere on the board
MODE_1: R10.2, SW1.2, U6.22 (PA13); also elsewhere on the board
MODE_2: J12.8, R9.2, SW1.3, U6.23 (PA14); also elsewhere on the board
unnamed: C1A1.2, C1B1.1, JP9.2 (B), R1.1, R2.1, U6.40 (~RESET)
unnamed: C13.1, D4.1 (GND), J13.6 (Shield), R8.2
unnamed: C17.1, U6.43 (VDDCORE)
unnamed: C20.1, JP6.1 (A), JP7.2 (C), X2.4 (Vdd)
unnamed: C21.2, EC6.1, FB2.2, U6.6 (VDDANA)
unnamed: C23.1, JP6.2 (C), X2.1 (TRI)
unnamed: C36.1, R41.1, U23.2, X2.3 (OUT)
unnamed: D4.4 (VCC), D5.2 (A), J13.1 (VBUS)
unnamed: D9.2 (A), R39.1
unnamed: J12.1, U6.13 (PA08)
unnamed: J12.2, U6.24 (PA15)
unnamed: J12.3, U6.32 (PA23)
unnamed: J12.4, U6.39 (PA27)
unnamed: J12.5, U6.41 (PA28)
unnamed: J12.6, U6.45 (PA30)
unnamed: N1.1 (A), SW1.4, SW1.5, SW1.6
PEND_ENABLE: J14.2, U7.5 (Q1); also elsewhere on the board
SERVO_1: A2.12 (D9), U6.29 (PA20); also elsewhere on the board
SERVO_2: J12.7, U6.46 (PA31); also elsewhere on the board
STEPP_EN: J14.8, U7.11 (Q7); also elsewhere on the board
SUP_LED1: A2.15 (D12), U6.28 (PA19); also elsewhere on the board
SUP_LED2: A2.10 (D7), U6.11 (PA06); also elsewhere on the board
USB_BUS: D5.1 (K); also elsewhere on the board

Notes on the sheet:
PCB Laid out for Either: - Arduino Nano 33 IoT OR - SAMD21 MCU Only components for 1 of these options should be populated, the other left emtpty Connectors in the middle are shared by both options and should always be populated
DIGITAL IN
External Clock Package IC
Should be low ESR
SAMD21 BareMetal USB I/F
Replicates LED_BUILTIN on Arduino Pin: D13
Arduino Nano IoT 33 Devboard Slot
Servo 2 can only work if MCU configured to use shift register outputs, else conflict with: STEPP_RESET
Supervisor MCU
Shift Register to Expand Number of Output Pins
SPI Header is then useable as GPIO
C1A or C1B IF C1B -> R1 = 10k
For Osc IC - R? Unpopulated - C? & C? Unpopulated - C? ~ 10n - All Jumpers 2 - 1 For Xtal - R? = 0ohm to 47ohm - C? & C? Value = 2 *(Cxtal -Cstray) - Omit C20 - All Jumpers 2 - 3 - TCYSH14F - No Idea, probably omit for Xtal
SAMD21 BareMetal MCU Slot
place shiftreg header and MCU header together - Shorting the pins CH by CH avoids the need for shift register if using raw MCU.
A4 & A5 Internal pull up for I2C Bus Avoid analogRead
Additional Ferrite Bead here?

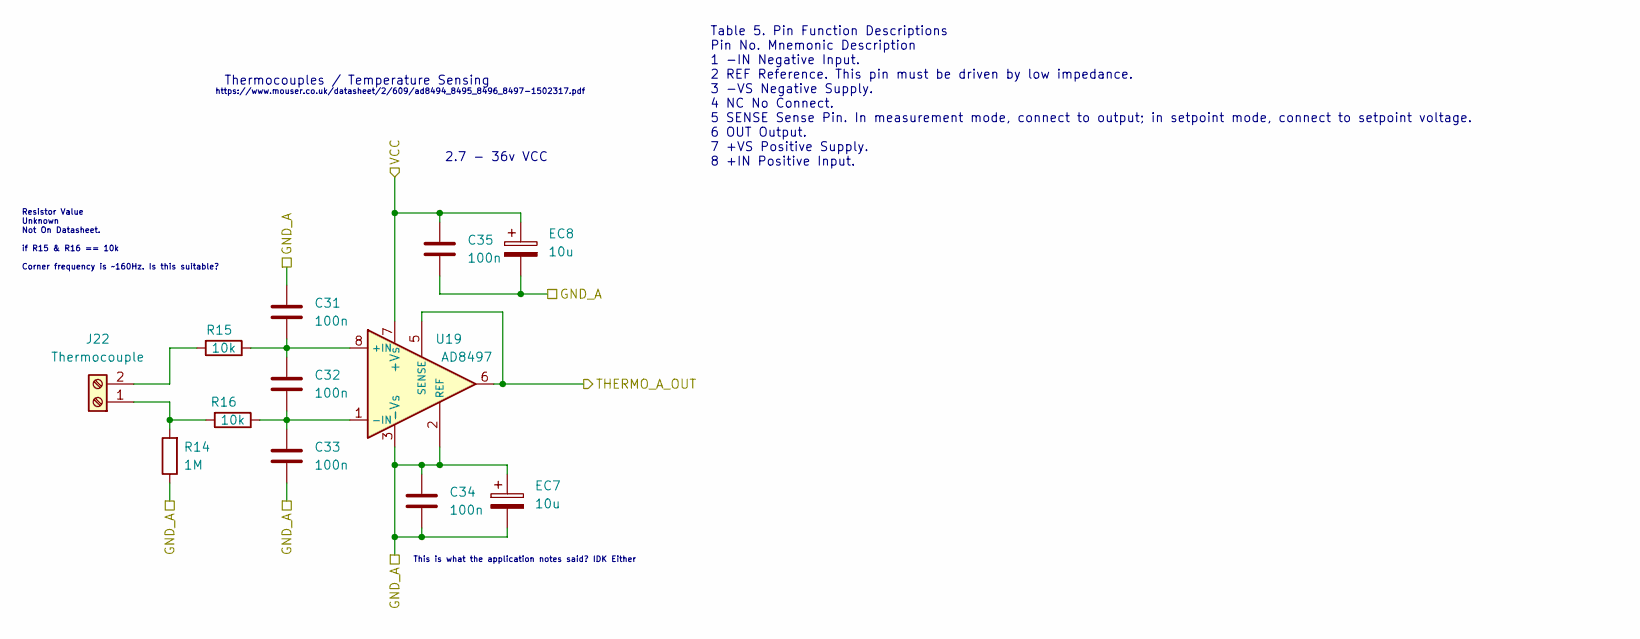
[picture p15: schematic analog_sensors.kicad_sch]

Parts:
C31, C32, C33, C34, C35: 100n; C_0805_2012Metric_Pad1.18x1.45mm_HandSolder
EC7, EC8: 10u; CP_Elec_4x5.4
J22: Thermocouple; TerminalBlock_Altech_AK300-2_P5.00mm
R14: 1M; R_0805_2012Metric_Pad1.20x1.40mm_HandSolder
R15, R16: 10k; R_0805_2012Metric_Pad1.20x1.40mm_HandSolder
U19: AD8497; MSOP-8_3x3mm_P0.65mm

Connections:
3V3_DC_MCU: C35.1, EC8.1, U19.7 (+Vs); also elsewhere on the board
/Analog Sensor Buffers/A_IN_C: U19.5 (SENSE), U19.6; also elsewhere on the board
GNDD: C31.1, C33.2, C34.1, C34.2, C35.2, EC7.1, EC7.2, EC8.2, R14.1, U19.2 (REF), U19.3 (-Vs); also elsewhere on the board
unnamed: C31.2, C32.1, R15.1, U19.8 (+IN)
unnamed: C32.2, C33.1, R16.1, U19.1 (-IN)
unnamed: J22.1, R14.2, R16.2
unnamed: J22.2, R15.2

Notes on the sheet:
Resistor Value Unknown Not On Datasheet. if R15 & R16 == 10k Corner frequency is ~160Hz. Is this suitable?
This is what the application notes said? IDK Either
Table 5. Pin Function Descriptions Pin No. Mnemonic Description 1 −IN Negative Input. 2 REF Reference. This pin must be driven by low impedance. 3 −VS Negative Supply. 4 NC No Connect. 5 SENSE Sense Pin. In measurement mode, connect to output; in setpoint mode, connect to setpoint voltage. 6 OUT Ou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
https://www.mouser.co.uk/datasheet/2/609/ad8494_8495_8496_8497-1502317.pdf
2.7 - 36v VCC
Thermocouples / Temperature Sensing

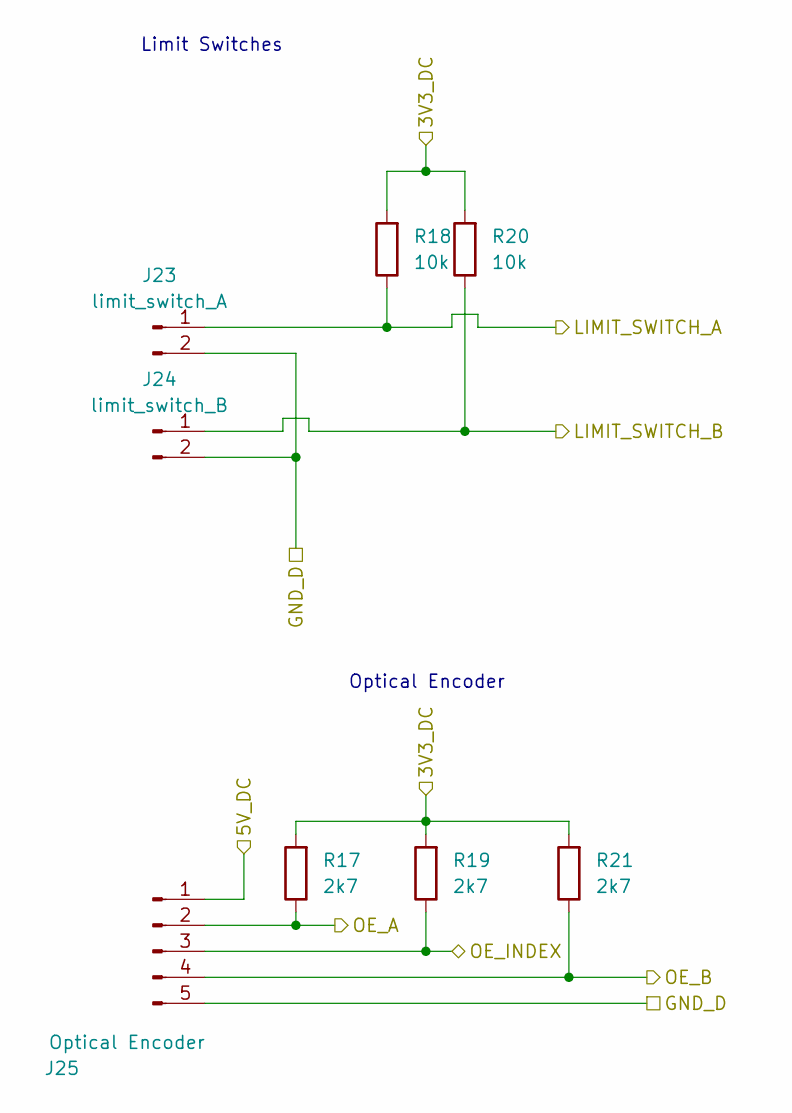
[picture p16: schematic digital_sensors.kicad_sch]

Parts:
J23: limit_switch_A; Molex_KK-254_AE-6410-02A_1x02_P2.54mm_Vertical
J24: limit_switch_B; Molex_KK-254_AE-6410-02A_1x02_P2.54mm_Vertical
J25: Optical Encoder; Molex_KK-254_AE-6410-05A_1x05_P2.54mm_Vertical
R17, R19, R21: 2k7; R_0805_2012Metric_Pad1.20x1.40mm_HandSolder
R18, R20: 10k; R_0805_2012Metric_Pad1.20x1.40mm_HandSolder

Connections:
3V3_DC_MCU: R17.2, R18.2, R19.2, R20.2, R21.2; also elsewhere on the board
5V_DC_RPI: J25.1; also elsewhere on the board
/Digital Sensor Buffers/D_IN_A: J23.1, R18.1; also elsewhere on the board
/Digital Sensor Buffers/D_IN_B: J24.1, R20.1; also elsewhere on the board
/Digital Sensor Buffers/D_IN_C: J25.2, R17.1; also elsewhere on the board
/Digital Sensor Buffers/D_IN_D: J25.3, R19.1; also elsewhere on the board
/Digital Sensor Buffers/D_IN_E: J25.4, R21.1; also elsewhere on the board
GNDD: J23.2, J24.2, J25.5; also elsewhere on the board

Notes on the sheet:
Optical Encoder
Limit Switches

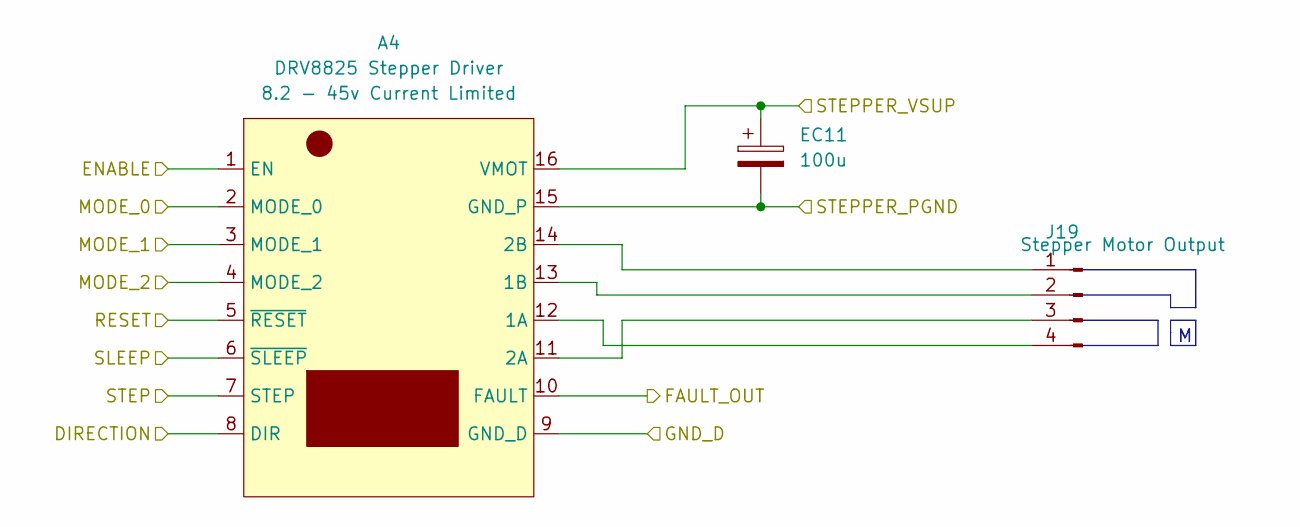
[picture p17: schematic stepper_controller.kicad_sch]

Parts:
A4: DRV8825 Stepper Driver; DRV8825 Stepper Motor Module
EC11: 100u; CP_Elec_6.3x7.7
J19: Stepper Motor Output; JST_XH_B4B-XH-A_1x04_P2.50mm_Vertical

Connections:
12V_DC_BUS: A4.16 (VMOT), EC11.1; also elsewhere on the board
/DC Motor Controller/PENDULUM_PIN_1: A4.7 (STEP); also elsewhere on the board
/Output Logic/DIRECTION_OUT: A4.8 (DIR); also elsewhere on the board
/Output Logic/STEP_RST_OUT: A4.5 (~RESET); also elsewhere on the board
/Output Logic/STEP_SLP_OUT: A4.6 (~SLEEP); also elsewhere on the board
GNDPWR: A4.9 (GND_D), A4.15 (GND_P), EC11.2; also elsewhere on the board
MODE_0: A4.2 (MODE_0); also elsewhere on the board
MODE_1: A4.3 (MODE_1); also elsewhere on the board
MODE_2: A4.4 (MODE_2); also elsewhere on the board
unnamed: A4.13 (1B), J19.2
unnamed: A4.14 (2B), J19.1
unnamed: A4.11 (2A), J19.3
unnamed: A4.12 (1A), J19.4
STEPP_EN: A4.1 (EN); also elsewhere on the board
STPPR_FAULT: A4.10 (FAULT); also elsewhere on the board

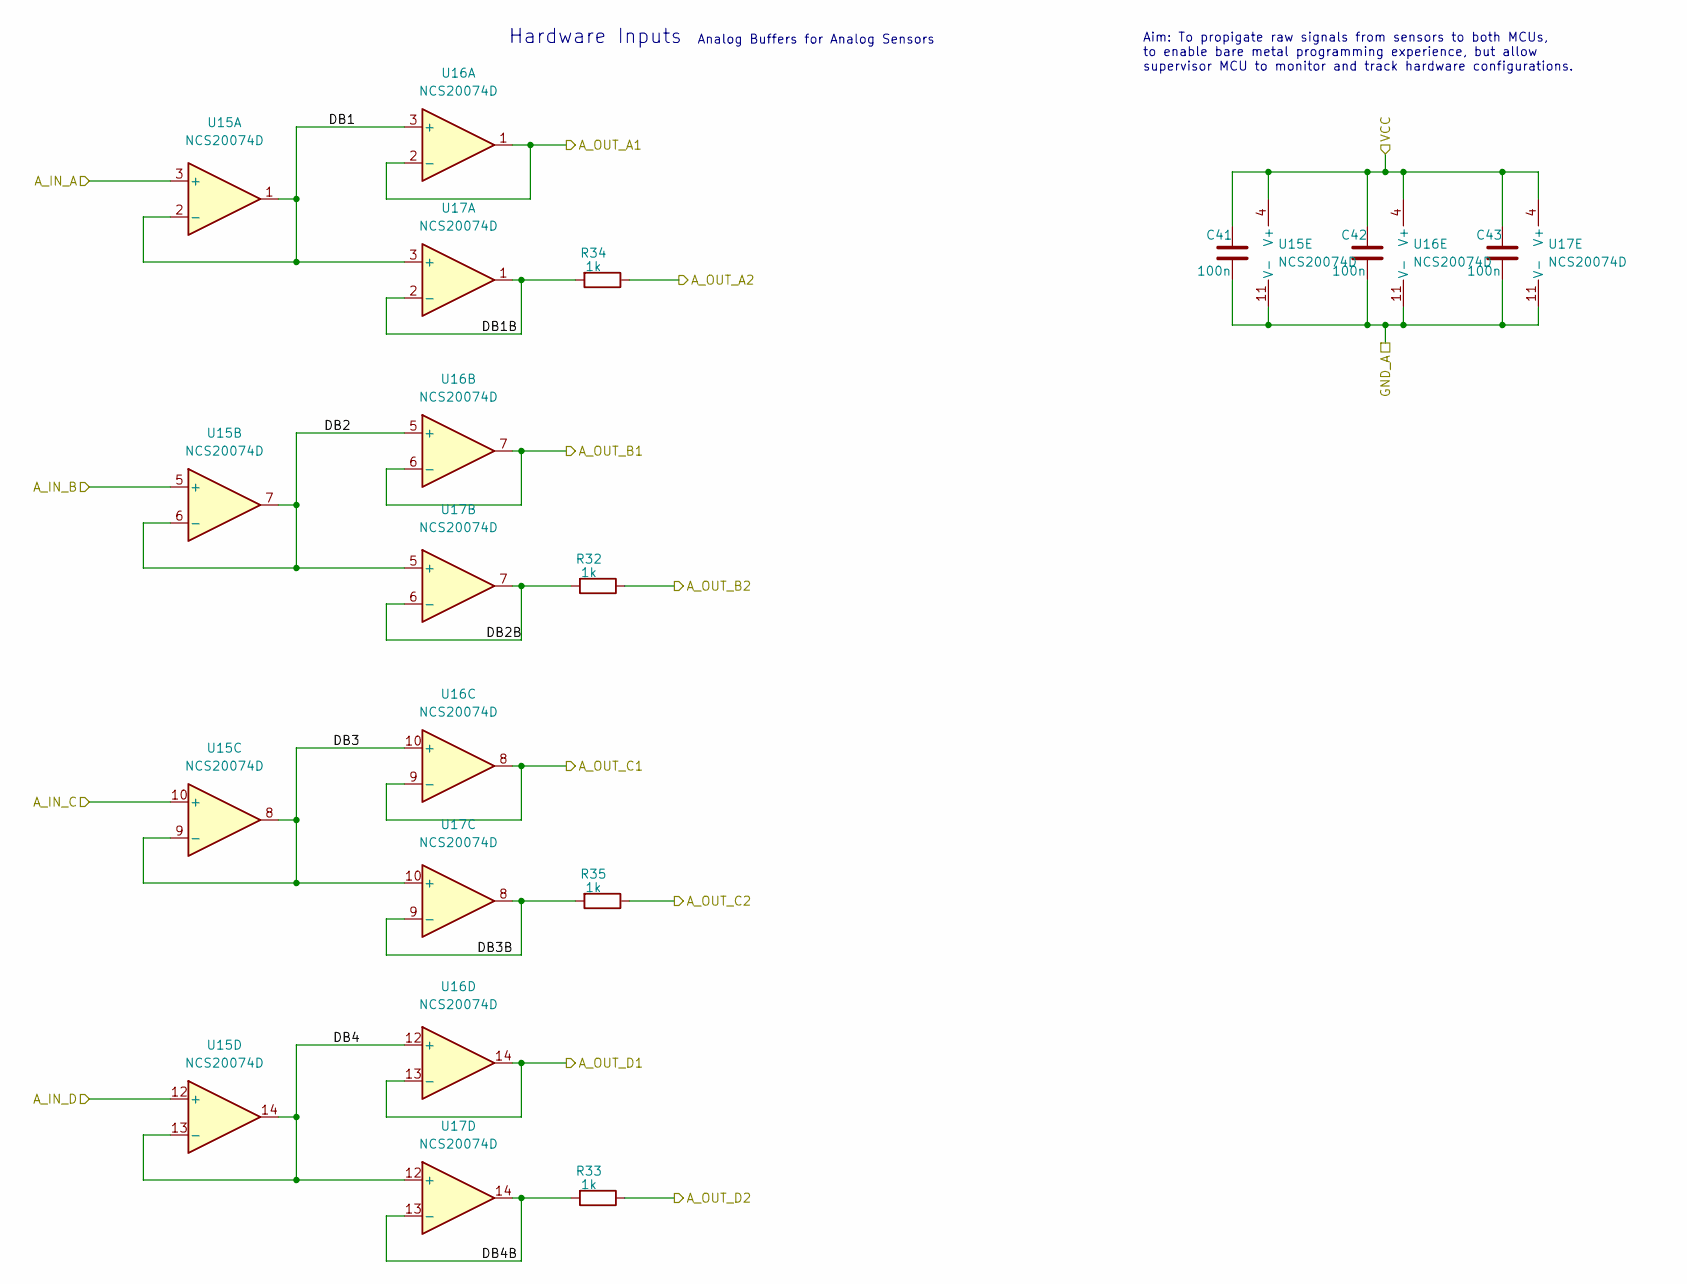
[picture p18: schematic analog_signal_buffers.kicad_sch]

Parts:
C41, C42, C43: 100n; C_0805_2012Metric_Pad1.18x1.45mm_HandSolder
R32, R33, R34, R35: 1k; R_0805_2012Metric_Pad1.20x1.40mm_HandSolder
U15, U16, U17: NCS20074D; SOIC-14_3.9x8.7mm_P1.27mm

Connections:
3V3_DC_MCU: C41.1, C42.1, C43.1, U15.4 (V+), U16.4 (V+), U17.4 (V+); also elsewhere on the board
/Analog Sensor Buffers/A_IN_C: U15.10 (+); also elsewhere on the board
/Analog Sensor Buffers/A_OUT_A1: U16.1, U16.2 (-); also elsewhere on the board
/Analog Sensor Buffers/A_OUT_A2: R34.1; also elsewhere on the board
/Analog Sensor Buffers/A_OUT_B1: U16.6 (-), U16.7; also elsewhere on the board
/Analog Sensor Buffers/A_OUT_B2: R32.1; also elsewhere on the board
/Analog Sensor Buffers/A_OUT_C1: U16.8, U16.9 (-); also elsewhere on the board
/Analog Sensor Buffers/A_OUT_C2: R35.1; also elsewhere on the board
/Analog Sensor Buffers/DB1: U15.1, U15.2 (-), U16.3 (+), U17.3 (+)
/Analog Sensor Buffers/DB1B: R34.2, U17.1, U17.2 (-)
/Analog Sensor Buffers/DB2: U15.6 (-), U15.7, U16.5 (+), U17.5 (+)
/Analog Sensor Buffers/DB2B: R32.2, U17.6 (-), U17.7
/Analog Sensor Buffers/DB3: U15.8, U15.9 (-), U16.10 (+), U17.10 (+)
/Analog Sensor Buffers/DB3B: R35.2, U17.8, U17.9 (-)
/Analog Sensor Buffers/DB4: U15.13 (-), U15.14, U16.12 (+), U17.12 (+)
/Analog Sensor Buffers/DB4B: R33.2, U17.13 (-), U17.14
A_BUFFER_IN: U15.12 (+); also elsewhere on the board
A_BUFFER_OUT_A: U16.13 (-), U16.14; also elsewhere on the board
A_BUFFER_OUT_B: R33.1; also elsewhere on the board
GNDD: C41.2, C42.2, C43.2, U15.11 (V-), U16.11 (V-), U17.11 (V-); also elsewhere on the board
M_I_SENSE_1: U15.3 (+); also elsewhere on the board
M_I_SENSE_2: U15.5 (+); also elsewhere on the board

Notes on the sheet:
Hardware Inputs
Analog Buffers for Analog Sensors
Aim: To propigate raw signals from sensors to both MCUs, to enable bare metal programming experience, but allow supervisor MCU to monitor and track hardware configurations.

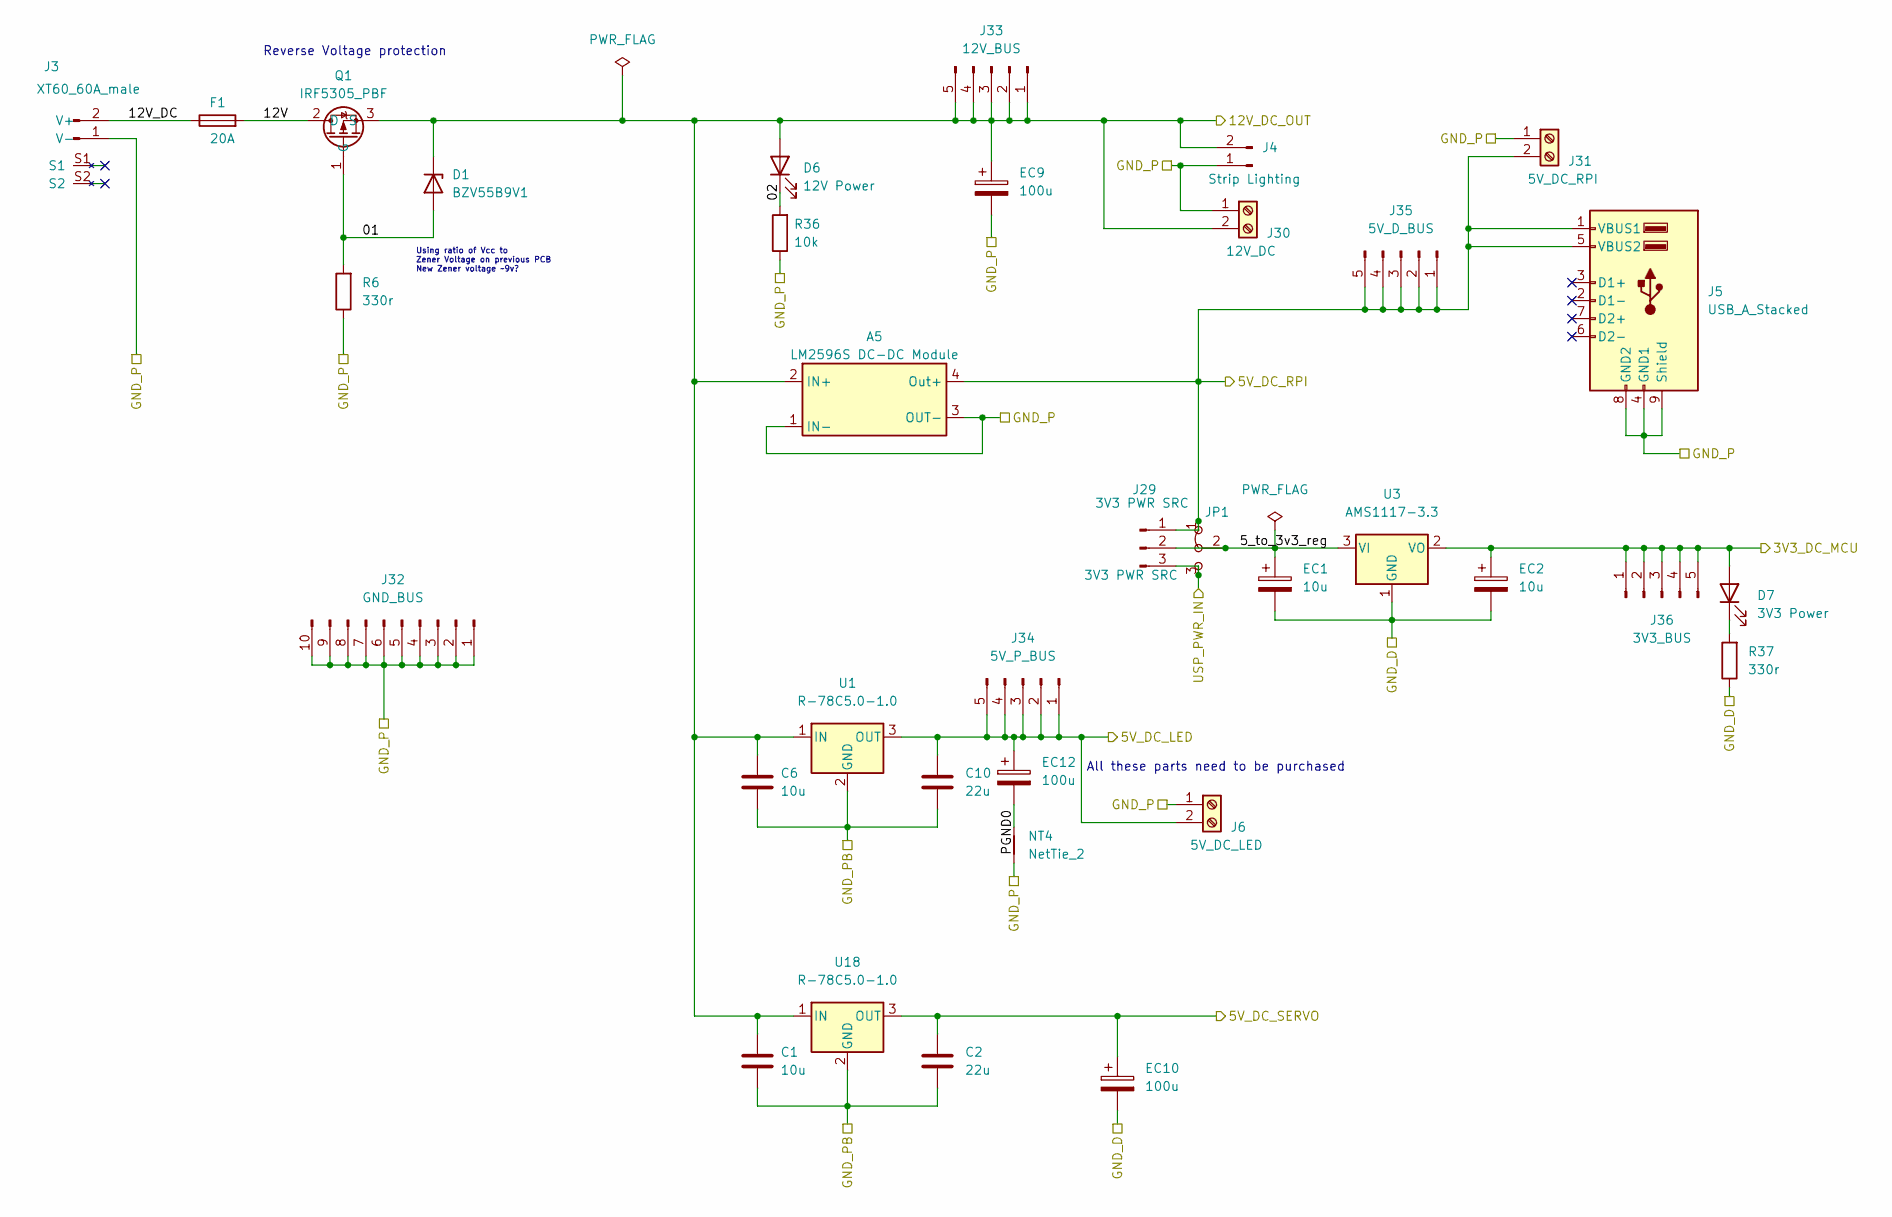
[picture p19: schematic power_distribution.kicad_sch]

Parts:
A5: LM2596S DC-DC Module
C1, C6: 10u; C_0805_2012Metric_Pad1.18x1.45mm_HandSolder
C2, C10: 22u; C_0805_2012Metric_Pad1.18x1.45mm_HandSolder
D1: BZV55B9V1; D_MiniMELF
D6: 12V Power; D_0805_2012Metric_Pad1.15x1.40mm_HandSolder
D7: 3V3 Power; D_0805_2012Metric_Pad1.15x1.40mm_HandSolder
EC1, EC2: 10u; CP_Elec_4x5.4
EC9, EC10, EC12: 100u; CP_Elec_6.3x7.7
F1: 20A; Fuseholder_Cylinder-5x20mm_Stelvio-Kontek_PTF78_Horizontal_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
J3: XT60_60A_male; AMASS_XT60PW-M
J4: Strip Lighting; Molex_KK-254_AE-6410-02A_1x02_P2.54mm_Vertical
J5: USB_A_Stacked; USB_A_Wuerth_61400826021_Horizontal_Stacked
J6: 5V_DC_LED; TerminalBlock_Altech_AK300-2_P5.00mm
J29: 3V3 PWR SRC; PinHeader_1x03_P2.54mm_Vertical
J30: 12V_DC; TerminalBlock_Altech_AK300-2_P5.00mm
J31: 5V_DC_RPI; TerminalBlock_Altech_AK300-2_P5.00mm
J32: GND_BUS; PinHeader_1x10_P1.27mm_Vertical
J33: 12V_BUS; PinHeader_1x05_P2.54mm_Vertical
J34: 5V_P_BUS; PinHeader_1x05_P2.54mm_Vertical
J35: 5V_D_BUS; PinHeader_1x05_P2.54mm_Vertical
J36: 3V3_BUS; PinHeader_1x05_P2.54mm_Vertical
JP1: 3V3 PWR SRC; SolderJumper-3_P1.3mm_Bridged12_RoundedPad1.0x1.5mm
NT4: NetTie_2; NetTie-2_SMD_Pad2.0mm
Q1: IRF5305_PBF; TO-220-3_Vertical
R6, R37: 330r; R_0805_2012Metric_Pad1.20x1.40mm_HandSolder
R36: 10k; R_0805_2012Metric_Pad1.20x1.40mm_HandSolder
U1, U18: R-78C5.0-1.0; Converter_DCDC_RECOM_R-78E-0.5_THT
U3: AMS1117-3.3; SOT-223-3_TabPin2

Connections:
3V3_DC_MCU: D7.2 (A), EC2.1, J36.1, J36.2, J36.3, J36.4, J36.5, U3.2 (VO); also elsewhere on the board
5V_DC_LED: C10.1, EC12.1, J6.2, J34.1, J34.2, J34.3, J34.4, J34.5, U1.3 (OUT); also elsewhere on the board
5V_DC_RPI: A5.4 (Out+), J5.1 (VBUS1), J5.5 (VBUS2), J29.1, J31.2, J35.1, J35.2, J35.3, J35.4, J35.5, JP1.1 (A); also elsewhere on the board
5V_DC_SERVO: C2.1, EC10.1, U18.3 (OUT); also elsewhere on the board
12V_DC_BUS: A5.2 (IN+), C1.1, C6.1, D1.1 (K), D6.2 (A), EC9.1, J4.2, J30.2, J33.1, J33.2, J33.3, J33.4, J33.5, Q1.3 (S), U1.1 (IN), U18.1 (IN); also elsewhere on the board
/Power Input & Distribution/01: D1.2 (A), Q1.1 (G), R6.2
/Power Input & Distribution/02: D6.1 (K), R36.2
/Power Input & Distribution/5_to_3v3_reg: EC1.1, J29.2, JP1.2 (C), U3.3 (VI)
/Power Input & Distribution/12V: F1.2, Q1.2 (D)
/Power Input & Distribution/12V_DC: F1.1, J3.2 (V+)
/Power Input & Distribution/PGND0: EC12.2, NT4.2
GNDD: EC1.2, EC2.2, EC10.2, R37.1, U3.1 (GND); also elsewhere on the board
GNDPWR: A5.1 (IN-), A5.3 (OUT-), EC9.2, J3.1 (V-), J4.1, J5.4 (GND1), J5.8 (GND2), J5.9 (Shield), J6.1, J30.1, J31.1, J32.1, J32.2, J32.3, J32.4, J32.5, J32.6, J32.7, J32.8, J32.9, J32.10, NT4.1, R6.1, R36.1; also elsewhere on the board
GND_PB: C1.2, C2.2, C6.2, C10.2, U1.2 (GND), U18.2 (GND); also elsewhere on the board
unnamed: D7.1 (K), R37.2
USB_BUS: J29.3, JP1.3 (B); also elsewhere on the board

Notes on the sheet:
Reverse Voltage protection
Using ratio of Vcc to Zener Voltage on previous PCB New Zener voltage ~9v?
All these parts need to be purchased

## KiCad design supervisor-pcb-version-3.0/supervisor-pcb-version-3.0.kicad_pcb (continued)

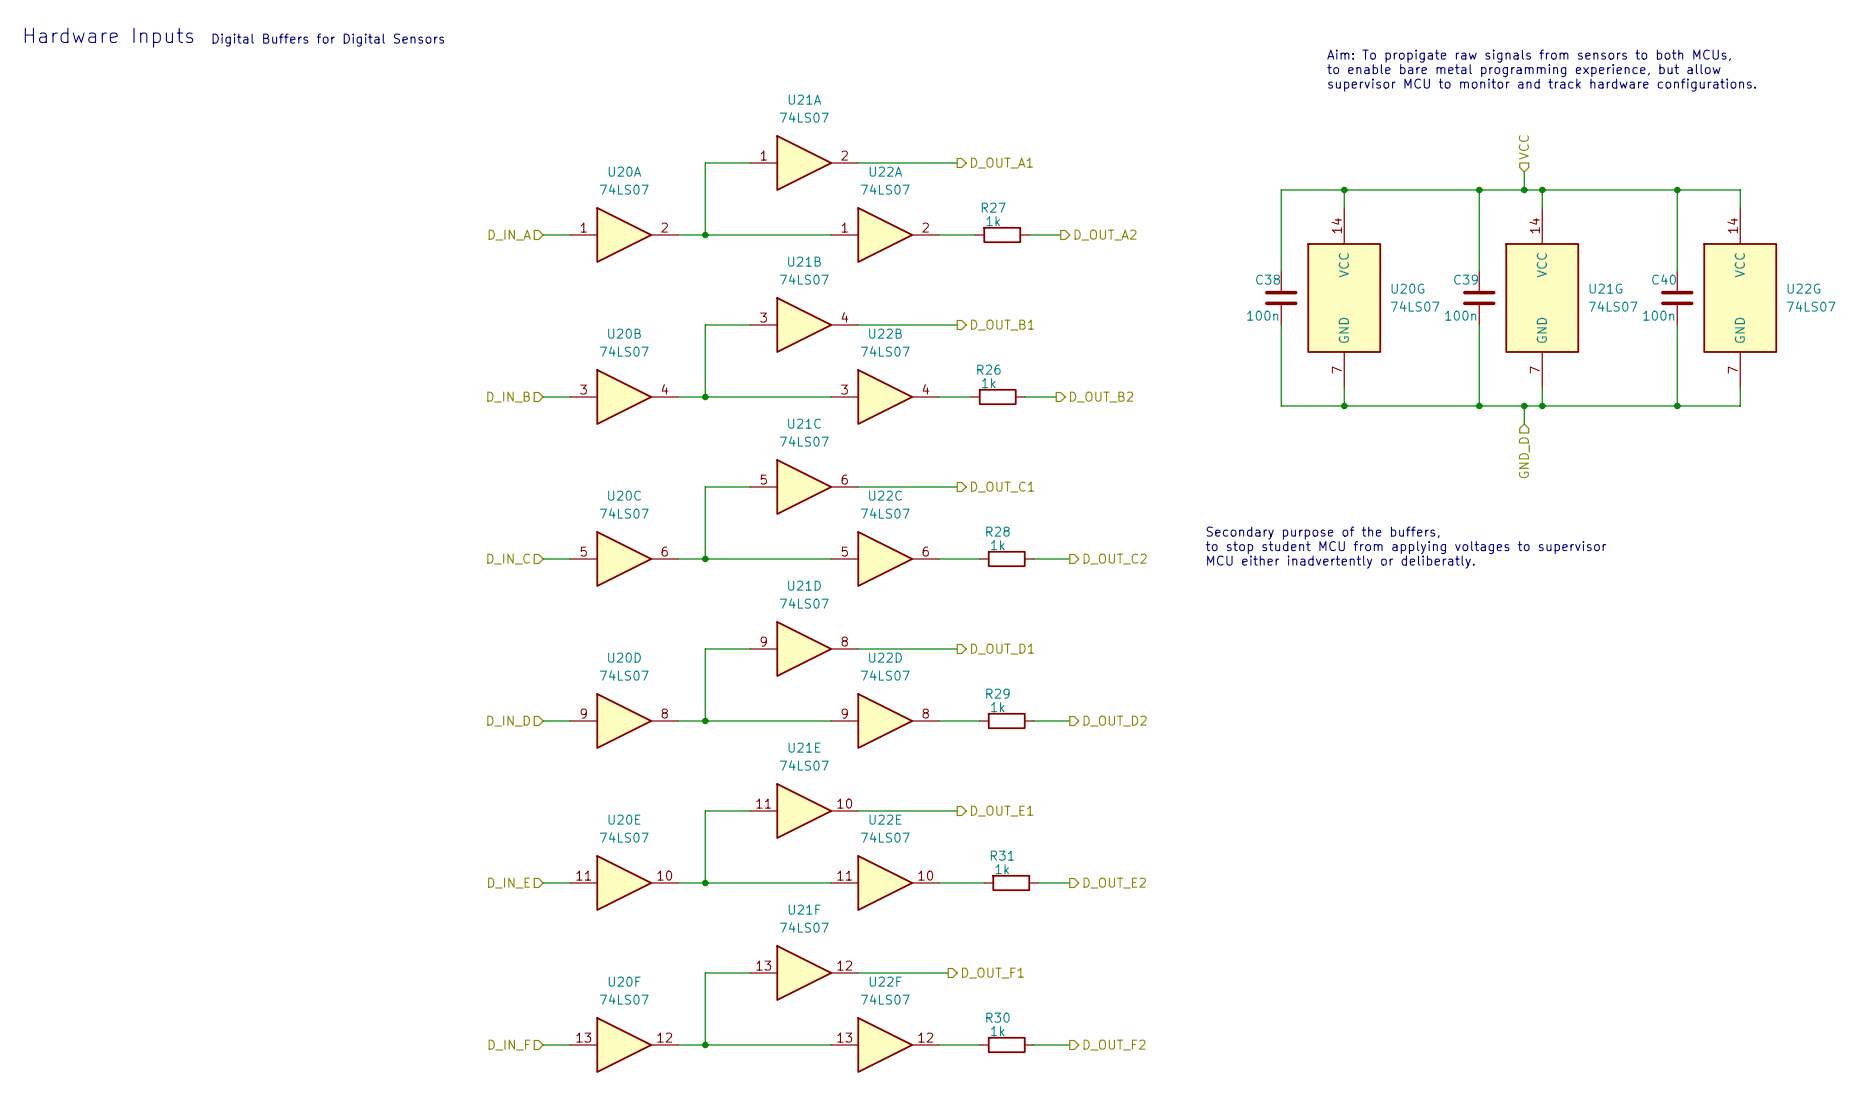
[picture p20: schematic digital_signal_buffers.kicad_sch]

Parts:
C38, C39, C40: 100n; C_0805_2012Metric_Pad1.18x1.45mm_HandSolder
R26, R27, R28, R29, R30, R31: 1k; R_0805_2012Metric_Pad1.20x1.40mm_HandSolder
U20, U21, U22: 74LS07; SOIC-14_3.9x8.7mm_P1.27mm

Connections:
3V3_DC_MCU: C38.1, C39.1, C40.1, U20.14 (VCC), U21.14 (VCC), U22.14 (VCC); also elsewhere on the board
/Digital Sensor Buffers/D_IN_A: U20.1; also elsewhere on the board
/Digital Sensor Buffers/D_IN_B: U20.3; also elsewhere on the board
/Digital Sensor Buffers/D_IN_C: U20.5; also elsewhere on the board
/Digital Sensor Buffers/D_IN_D: U20.9; also elsewhere on the board
/Digital Sensor Buffers/D_IN_E: U20.11; also elsewhere on the board
/Digital Sensor Buffers/D_OUT_A1: U21.2; also elsewhere on the board
/Digital Sensor Buffers/D_OUT_B1: U21.4; also elsewhere on the board
/Digital Sensor Buffers/D_OUT_C1: U21.6; also elsewhere on the board
/Digital Sensor Buffers/D_OUT_D1: U21.8; also elsewhere on the board
/Digital Sensor Buffers/D_OUT_E1: U21.10; also elsewhere on the board
/Digital Sensor Buffers/D_OUT_F1: U21.12; also elsewhere on the board
GNDD: C38.2, C39.2, C40.2, U20.7 (GND), U21.7 (GND), U22.7 (GND); also elsewhere on the board
LIMIT_1: R27.1; also elsewhere on the board
LIMIT_2: R26.1; also elsewhere on the board
unnamed: R26.2, U22.4
unnamed: R27.2, U22.2
unnamed: R28.2, U22.6
unnamed: R29.2, U22.8
unnamed: R30.2, U22.12
unnamed: R31.2, U22.10
unnamed: U20.2, U21.1, U22.1
unnamed: U20.4, U21.3, U22.3
unnamed: U20.6, U21.5, U22.5
unnamed: U20.8, U21.9, U22.9
unnamed: U20.10, U21.11, U22.11
unnamed: U20.12, U21.13, U22.13
OE_A: R28.1; also elsewhere on the board
OE_B: R31.1; also elsewhere on the board
OE_IDX: R29.1; also elsewhere on the board
STPPR_FAULT: U20.13; also elsewhere on the board
STU_STP_FLT: R30.1; also elsewhere on the board

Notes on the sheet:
Hardware Inputs
Digital Buffers for Digital Sensors
Secondary purpose of the buffers, to stop student MCU from applying voltages to supervisor MCU either inadvertently or deliberatly.
Aim: To propigate raw signals from sensors to both MCUs, to enable bare metal programming experience, but allow supervisor MCU to monitor and track hardware configurations.

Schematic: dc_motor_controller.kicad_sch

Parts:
A3: Infineon Motor Shield Uno; Infineon Motor Sheild hiddenPins
F2: 2A; Fuseholder_Cylinder-5x20mm_Stelvio-Kontek_PTF78_Horizontal_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
J16: DC Motor PWR; TerminalBlock_Altech_AK300-2_P5.00mm
J17: MotorController Output; TerminalBlock_Altech_AK300-3_P5.00mm
J18: DC Motor Output; TerminalBlock_Altech_AK300-3_P5.00mm
R12, R13: 470r; R_0805_2012Metric_Pad1.20x1.40mm_HandSolder

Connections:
5V_DC_SERVO: A3.5 (5V); also elsewhere on the board
12V_DC_BUS: F2.1; also elsewhere on the board
/DC Motor Controller/ENABLE: A3.27 (INH_1), A3.28 (INH_2); also elsewhere on the board
/DC Motor Controller/HC: F2.2, J16.1
/DC Motor Controller/HC1: J17.3, J18.1
/DC Motor Controller/HC2: J17.2, J18.2
/DC Motor Controller/HC3: J17.1, J18.3
/DC Motor Controller/IN_1: A3.18 (IN_1); also elsewhere on the board
/DC Motor Controller/IN_2: A3.26 (IN_2); also elsewhere on the board
/DC Motor Controller/PENDULUM_PIN_1: A3.19 (D4); also elsewhere on the board
GNDD: A3.6 (GND), A3.7 (GND), A3.29 (GND), R12.1, R13.1; also elsewhere on the board
GNDPWR: J16.2; also elsewhere on the board
M_I_SENSE_1: A3.9 (IS_1), R12.2; also elsewhere on the board
M_I_SENSE_2: A3.10 (IS_2), R13.2; also elsewhere on the board
PEND_ENABLE: A3.20 (D5); also elsewhere on the board
SERVO_1: A3.24 (D9); also elsewhere on the board
STUDNT_LED1: A3.21 (D6); also elsewhere on the board
STUDNT_LED2: A3.22 (D7); also elsewhere on the board
STUDNT_LED3: A3.23 (D8); also elsewhere on the board
SUP_LED1: A3.25 (D10); also elsewhere on the board
SUP_LED2: A3.17 (D2); also elsewhere on the board

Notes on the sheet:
If the high side drain current is zero (ISD(HS) = 0A) the offset current IIS = IIS(offset) still will be driven. The external resistor RIS determines the voltage per IS output current. The voltage can be calculated by VIS = RIS . IIS. In case of a fault condition the status output is connected to a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
Current sense outputs: I(load) = dk(ilis)*(I(is)-I(is_offset)) Differential Current Sense ratio dk(ilis): dk(ilis) = (I(L2)-I(L1))/((I(is))*(I(L2))-(I(is)*(I(L1)))
Assume 6.5mA MAX V = 6.5 * 500 / 1000 V = 3.25v
These Pins are connected OFF BOARD with wire
Must be 1% tolerance for 3.3v max
INH is active low, so renamed as ENABLE (Active HIGH to enable)
I(is_lim) @ Vs = 12v & Tj = 100degC = 5.25 mA
INH Pins can be joined
None of these pins are connected on Infineon Board

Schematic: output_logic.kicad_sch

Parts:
C24, C25, C26, C27, C28, C29, C30: 100n; C_0805_2012Metric_Pad1.18x1.45mm_HandSolder
U8: 4069; SOIC-14_3.9x8.7mm_P1.27mm
U9, U10, U11, U12: 4081; SOIC-14_3.9x8.7mm_P1.27mm
U13, U14: 74HC86; SOIC-14_3.9x8.7mm_P1.27mm

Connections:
3V3_DC_MCU: C24.1, C25.1, C26.1, C27.1, C28.1, C29.1, C30.1, U8.14 (VDD), U9.14 (VDD), U10.14 (VDD), U11.14 (VDD), U12.14 (VDD), U13.14 (VCC), U14.14 (VCC); also elsewhere on the board
/DC Motor Controller/ENABLE: U14.6; also elsewhere on the board
/DC Motor Controller/IN_1: U9.3; also elsewhere on the board
/DC Motor Controller/IN_2: U9.10; also elsewhere on the board
/DC Motor Controller/PENDULUM_PIN_1: U13.6; also elsewhere on the board
/Output Logic/DIRECTION_OUT: U13.3; also elsewhere on the board
/Output Logic/MCU_PIXEL_SELECT: U8.5, U12.9; also elsewhere on the board
/Output Logic/MCU_STEP_SELECT: U8.3, U10.2, U10.6, U10.9, U10.13; also elsewhere on the board
/Output Logic/PIXEL_DATA_OUT: U14.8; also elsewhere on the board
/Output Logic/STEP_RST_OUT: U13.11; also elsewhere on the board
/Output Logic/STEP_SLP_OUT: U13.8; also elsewhere on the board
/Output Logic/STUDENT_DIRECTION: U10.1; also elsewhere on the board
/Output Logic/STUDENT_MOTOR_EN: U12.5; also elsewhere on the board
/Output Logic/STUDENT_MOTOR_PWM: U12.1; also elsewhere on the board
/Output Logic/STUDENT_PIXEL_DATA: U12.8; also elsewhere on the board
/Output Logic/STUDENT_STEP: U10.5; also elsewhere on the board
/Output Logic/STUDENT_STEP_RST: U10.12; also elsewhere on the board
/Output Logic/STUDENT_STEP_SLP: U10.8; also elsewhere on the board
/Output Logic/SUPERVISOR_DIRECTION: U11.1; also elsewhere on the board
/Output Logic/SUPERVISOR_MOTOR_EN: U9.12; also elsewhere on the board
/Output Logic/SUPERVISOR_MOTOR_PWM: U9.5; also elsewhere on the board
/Output Logic/SUPERVISOR_PIXEL_DATA: U12.12; also elsewhere on the board
/Output Logic/SUPERVISOR_STEP: U11.5; also elsewhere on the board
/Output Logic/SUPERVISOR_STEP_RST: U11.12; also elsewhere on the board
/Output Logic/SUPERVISOR_STEP_SLP: U11.8; also elsewhere on the board
GNDD: C24.2, C25.2, C26.2, C27.2, C28.2, C29.2, C30.2, U8.7 (VSS), U8.9, U8.11, U8.13, U9.7 (VSS), U10.7 (VSS), U11.7 (VSS), U12.7 (VSS), U13.7 (GND), U14.7 (GND), U14.12, U14.13; also elsewhere on the board
unnamed: U8.2, U9.6, U9.13
unnamed: U10.3, U13.1
unnamed: U10.4, U13.4
unnamed: U10.10, U13.9
unnamed: U10.11, U13.12
unnamed: U11.3, U13.2
unnamed: U11.4, U13.5
unnamed: U11.10, U13.10
unnamed: U11.11, U13.13
unnamed: U8.4, U11.2, U11.6, U11.9, U11.13
unnamed: U12.3, U14.1
unnamed: U12.4, U14.4
unnamed: U12.10, U14.9
unnamed: U12.11, U14.10
unnamed: U8.6, U12.13
unnamed: U9.4, U14.2
unnamed: U9.1, U9.8, U14.3
unnamed: U9.11, U14.5
PEND_ENABLE: U8.1, U12.2, U12.6; also elsewhere on the board
SUP_LED1: U9.2; also elsewhere on the board
SUP_LED2: U9.9; also elsewhere on the board

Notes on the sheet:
Pixel Output
Hardware Outputs
Decoupling Caps
Stepper Motor Outputs
Aim: To give supervisor MCU ability to block control of experimental hardware by the student MCU, and allow supervisor MCU master control of all experimental hardware.
DC Motor Outputs
Spare Gates
PWM is assigned to either Motor driver board IN_1 or IN_2 based on 2 direction pins sent by Supervisor MCU. This would allow supervisor to drive both pins high, leading to SHOOT THROUGH. Student has the same inputs to motor driver, but direction pins are spoofed through the supervisor, so superviso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
Supervisor also controls whether PWM control is enabled from student MCU

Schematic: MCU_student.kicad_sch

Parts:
A1: Arduino_Nano_33_IoT; Arduino_Nano
C2A1: 100p; C_0805_2012Metric_Pad1.18x1.45mm_HandSolder
C2B1, C4, C8, C9, C11, C12: 100n; C_0805_2012Metric_Pad1.18x1.45mm_HandSolder
C3: 4n7; C_0805_2012Metric_Pad1.18x1.45mm_HandSolder
C5: 10n; C_0805_2012Metric_Pad1.18x1.45mm_HandSolder
C7: 1u; CP_EIA-2012-12_Kemet-R_Pad1.30x1.05mm_HandSolder
C14, C15: 12p; C_0805_2012Metric_Pad1.18x1.45mm_HandSolder
D2: PMEG6020ER; Nexperia_CFP3_SOD-123W
D3: PRTR5V0U2X; SOT-143
D8: Yellow; D_0805_2012Metric_Pad1.15x1.40mm_HandSolder
EC3, EC4: 10u; CP_Elec_4x5.4
FB1: BLM18PG471; L_0805_2012Metric_Pad1.05x1.20mm_HandSolder
J7: USB_B_Mini; USB_Mini-B_Lumberg_2486_01_Horizontal
J8: MCU_Header; PinHeader_1x08_P2.54mm_Vertical
J9: Spare Student GPIOs; PinHeader_1x04_P2.54mm_Vertical
J10: ShiftReg_Header; PinHeader_1x08_P2.54mm_Vertical
J11: SPI Student; PinHeader_1x03_P2.54mm_Vertical
J28: student_PA03; PinHeader_1x01_P1.27mm_Vertical
JP3, JP4: Xtal/IC; SolderJumper-3_P1.3mm_Bridged12_RoundedPad1.0x1.5mm_NumberL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
JP10: Reset GND; SolderJumper-2_P1.3mm_Open_Pad1.0x1.5mm
R3: 2k2; R_0805_2012Metric_Pad1.20x1.40mm_HandSolder
R4, R38: 330r; R_0805_2012Metric_Pad1.20x1.40mm_HandSolder
R7: 1M; R_0805_2012Metric_Pad1.20x1.40mm_HandSolder
R40: 0r; R_0805_2012Metric_Pad1.20x1.40mm_HandSolder
SW2: Student Reset; SW_Push_1P1T_NO_CK_KSC6xxJ
U2: TCYSH14F; SOT-23-5_HandSoldering
U4: ATSAMD21G18A-M; QFN-48-1EP_7x7mm_P0.5mm_EP5.15x5.15mm
U5: 4094; SOIC-16_3.9x9.9mm_P1.27mm
X1: 32.768kHz; Oscillator_SMD_Abracon_ASE-4Pin_3.2x2.5mm

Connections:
3V3_DC_MCU: A1.17 (3V3), C2A1.1, C4.1, C8.1, C9.2, C12.1, EC3.1, FB1.1, JP4.1 (A), R3.2, U2.5 (VCC), U4.17 (VDDIO), U4.36 (VDDIO), U4.44 (VDDIN), U5.15 (OE), U5.16 (VCC); also elsewhere on the board
/Analog Sensor Buffers/A_OUT_A2: A1.26 (A7), U4.48 (PB03); also elsewhere on the board
/Analog Sensor Buffers/A_OUT_B2: A1.25 (A6), U4.14 (PA09); also elsewhere on the board
/Analog Sensor Buffers/A_OUT_C2: A1.22 (A3), U4.15 (PA10); also elsewhere on the board
/Output Logic/STUDENT_DIRECTION: J10.5, U5.14 (Q4); also elsewhere on the board
/Output Logic/STUDENT_MOTOR_EN: J10.1, U5.4 (Q0); also elsewhere on the board
/Output Logic/STUDENT_MOTOR_PWM: A1.13 (D10), U4.30 (PA21); also elsewhere on the board
/Output Logic/STUDENT_PIXEL_DATA: A1.8 (D5), U4.10 (PA05); also elsewhere on the board
/Output Logic/STUDENT_STEP: A1.9 (D6), U4.9 (PA04); also elsewhere on the board
/Output Logic/STUDENT_STEP_RST: J10.7, U5.12 (Q6); also elsewhere on the board
/Output Logic/STUDENT_STEP_SLP: J10.6, U5.13 (Q5); also elsewhere on the board
/Student MCU/DC_MOTOR_DIR1: A1.15 (D12), U4.28 (PA19); also elsewhere on the board
/Student MCU/DC_MOTOR_DIR2: A1.10 (D7), U4.11 (PA06); also elsewhere on the board
/Student MCU/HSE_IN: JP3.3 (B), U2.4, U4.1 (PA00)
/Student MCU/HSE_OUT: R40.2, U4.2 (PA01)
/Student MCU/LATCH: A1.11 (D8), J11.3, U4.27 (PA18), U5.1 (STROBE)
/Student MCU/MCU_RESET: A1.3 (~RESET), A1.28 (~RESET), R4.2, SW2.2; also elsewhere on the board
/Student MCU/MODE_2: J8.8, U4.23 (PA14)
/Student MCU/MOSI: A1.14 (D11), J11.1, U4.25 (PA16), U5.2 (DATA)
/Student MCU/PROG_RX: A1.2 (D0/RX), U4.38 (PB23); also elsewhere on the board
/Student MCU/PROG_TX: A1.1 (D1/TX), U4.37 (PB22); also elsewhere on the board
/Student MCU/SCK: A1.16 (D13), J11.2, R38.2, U4.26 (PA17), U5.3 (CLOCK)
/Student MCU/SERVO_1: A1.12 (D9), U4.29 (PA20); also elsewhere on the board
/Student MCU/SERVO_2: U4.21 (PA12); also elsewhere on the board
/Student MCU/SHIFT_1: J10.2, U5.5 (Q1)
/Student MCU/SHIFT_2: J10.3, U5.6 (Q2)
/Student MCU/SHIFT_3: J10.4, U5.7 (Q3)
/Student MCU/SHIFT_7: J10.8, U5.11 (Q7)
/Student MCU/SPARE_3: J9.4, U4.22 (PA13)
/Student MCU/USB_N: D3.3 (I/O2), J7.2 (D-), U4.33 (PA24)
/Student MCU/USB_P: D3.2 (I/O1), J7.3 (D+), U4.34 (PA25)
GNDD: A1.4 (GND), A1.29 (GND), C2B1.2, C3.2, C4.2, C5.2, C7.2, C8.2, C9.1, C11.1, C12.2, C14.2, C15.2, D8.1 (K), EC3.2, EC4.2, J7.5 (GND), JP4.3 (B), JP10.1 (A), R7.1, SW2.1, U2.3 (GND), U4.5 (GNDANA), U4.18 (GND), U4.35 (GND), U4.42 (GND), U4.49 (EP), U5.8 (GND), X1.2 (GND); also elsewhere on the board
LIMIT_1: A1.23 (A4), U4.7 (PB08); also elsewhere on the board
LIMIT_2: U4.31 (PA22); also elsewhere on the board
unnamed: C2A1.2, C2B1.1, JP10.2 (B), R3.1, R4.1, U4.40 (~RESET)
unnamed: C3.1, D3.1 (GND), J7.6 (Shield), R7.2
unnamed: C5.1, JP3.1 (A), JP4.2 (C), X1.4 (Vdd)
unnamed: C7.1, U4.43 (VDDCORE)
unnamed: C11.2, EC4.1, FB1.2, U4.6 (VDDANA)
unnamed: C14.1, JP3.2 (C), X1.1 (TRI)
unnamed: C15.1, R40.1, U2.2, X1.3 (OUT)
unnamed: D2.2 (A), D3.4 (VCC), J7.1 (VBUS)
unnamed: D8.2 (A), R38.1
unnamed: J8.1, U4.13 (PA08)
unnamed: J8.2, U4.24 (PA15)
unnamed: J8.3, U4.32 (PA23)
unnamed: J8.4, U4.39 (PA27)
unnamed: J8.5, U4.41 (PA28)
unnamed: J8.6, U4.45 (PA30)
unnamed: J8.7, U4.46 (PA31)
unnamed: J28.1, U4.4 (PA03)
OE_A: A1.6 (D3), U4.20 (PB11); also elsewhere on the board
OE_B: A1.5 (D2), U4.19 (PB10); also elsewhere on the board
OE_IDX: A1.7 (D4), U4.12 (PA07); also elsewhere on the board
STUDNT_LED1: A1.21 (A2), J9.3, U4.16 (PA11); also elsewhere on the board
STUDNT_LED2: A1.20 (A1), J9.2, U4.47 (PB02); also elsewhere on the board
STUDNT_LED3: A1.19 (A0), J9.1, U4.3 (PA02); also elsewhere on the board
STU_STP_FLT: A1.24 (A5), U4.8 (PB09); also elsewhere on the board
USB_BUS: D2.1 (K); also elsewhere on the board

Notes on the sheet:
SAMD21 BareMetal MCU Slot
Shift Register to Expand Number of Output Pins
Functions Available on Raw MCU Removed for IoT Board to free pins
A4 & A5 Internal pull up for I2C Bus Avoid analogRead
PCB Laid out for Either: - Arduino Nano 33 IoT OR - SAMD21 MCU Only components for 1 of these options should be populated, the other left emtpty Connectors in the middle are shared by both options and should always be populated
Should be low ESR
For Osc IC - R? Unpopulated - C? & C? Unpopulated - C? ~ 10n - All Jumpers 2 - 1 For Xtal - R? = 0ohm to 47ohm - C? & C? Value = 2 *(Cxtal -Cstray) - All Jumpers 2 - 3 TCYSH14F - No Idea, probably omit for Xtal
Main Differences: No need for "Student Enable pins" as this is a supervisor only function No need for any pins that detect input from student No Mode Pins
Additional Ferrite Bead here?
C2A or C2B IF C2B -> R3 = 10k
External Clock Package IC
Student MCU
Arduino Nano IoT 33 Devboard Slot
SAMD21 BareMetal USB I/F
Replicates LED_BUILTIN on Arduino Pin: D13

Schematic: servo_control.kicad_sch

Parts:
J20: Servo_A; PinHeader_1x03_P2.54mm_Vertical
J21: Servo_B; PinHeader_1x03_P2.54mm_Vertical

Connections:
5V_DC_SERVO: J20.2, J21.2; also elsewhere on the board
GNDD: J20.3, J21.3; also elsewhere on the board
SERVO_1: J20.1; also elsewhere on the board
SERVO_2: J21.1; also elsewhere on the board

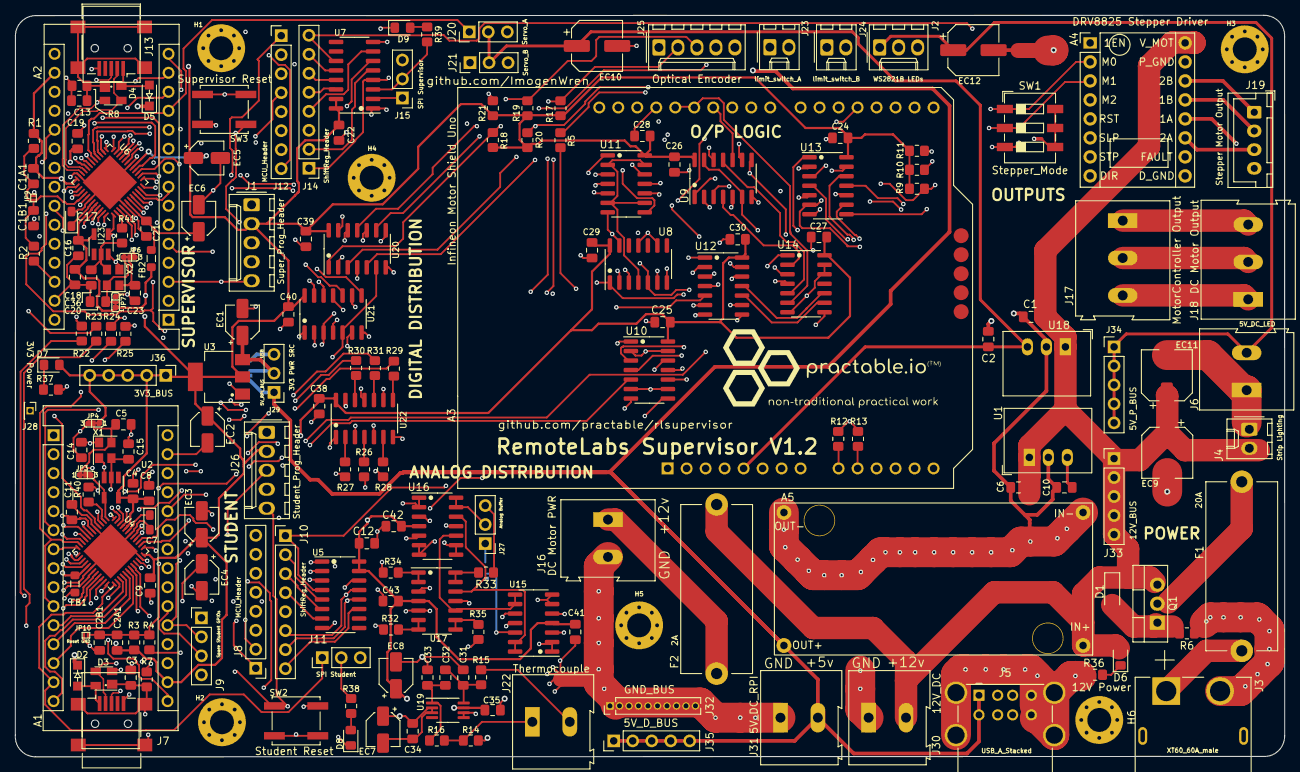
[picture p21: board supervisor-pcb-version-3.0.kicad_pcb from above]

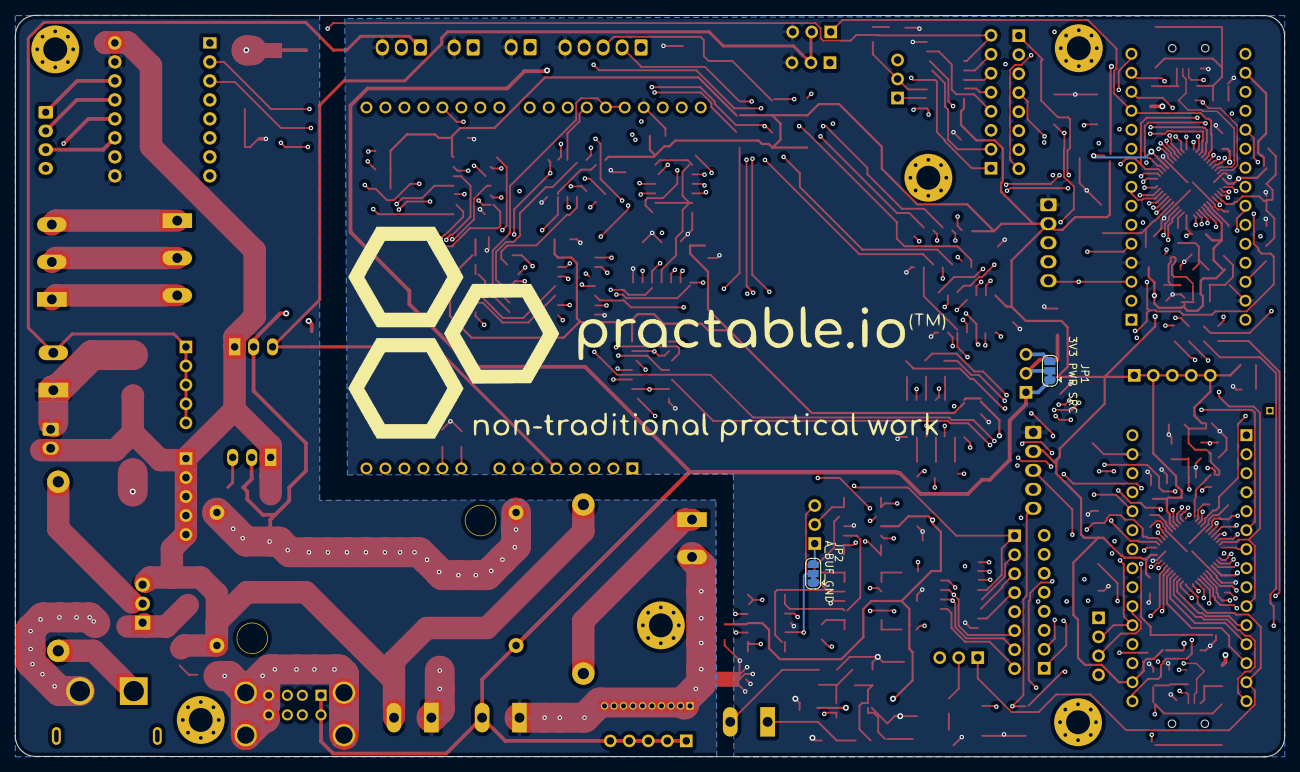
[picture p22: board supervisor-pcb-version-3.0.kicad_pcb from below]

Board: 4 copper layers, 169.7 x 99.1 mm, 200 parts (2 on the bottom side), 201 nets.

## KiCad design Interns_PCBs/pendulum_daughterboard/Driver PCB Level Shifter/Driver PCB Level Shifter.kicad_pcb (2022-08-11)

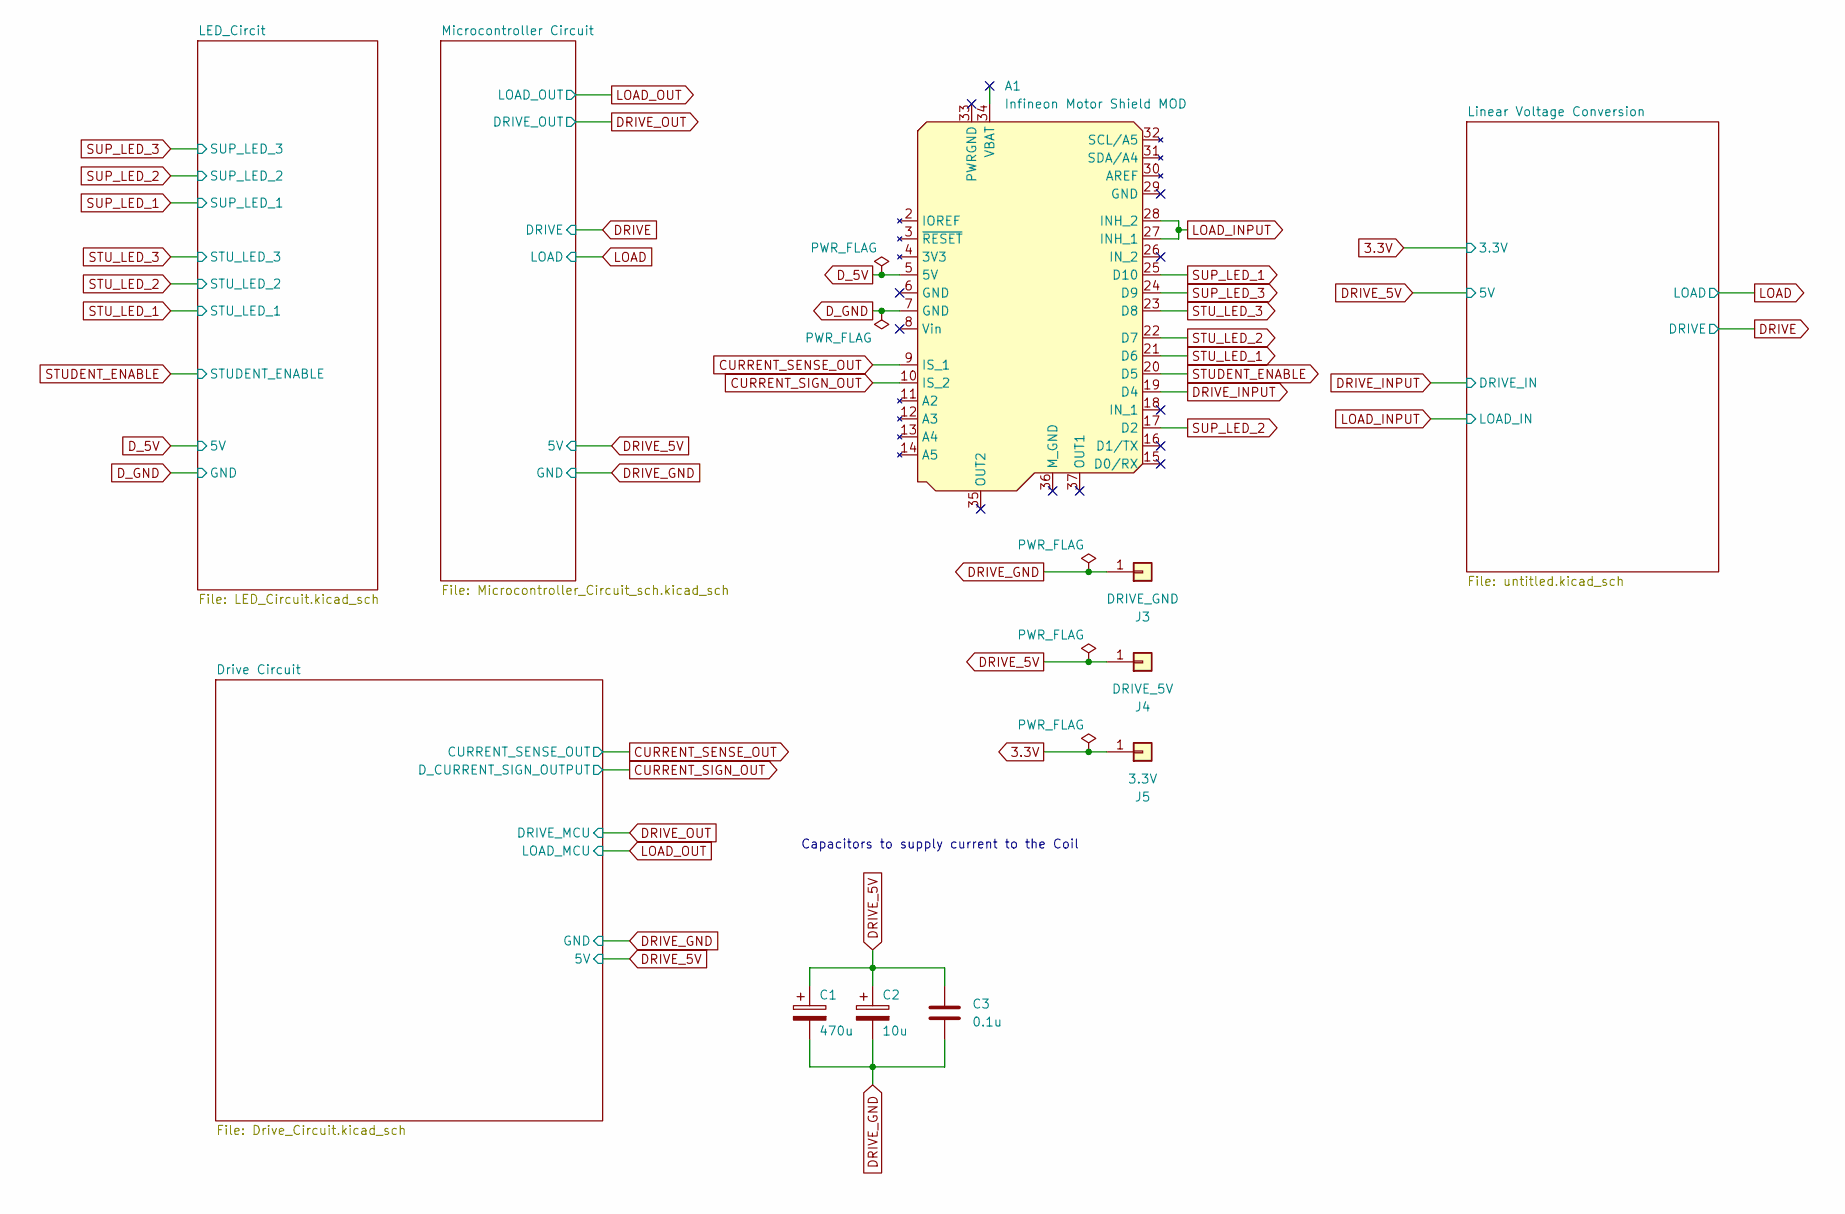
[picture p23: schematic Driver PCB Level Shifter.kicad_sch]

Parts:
A1: Infineon Motor Shield MOD; Infineon Motor Sheild hiddenPins
C1: 470u; C_Elec_8x10.2
C2: 10u; CP_Elec_3x5.3
C3: 0.1u; C_0805_2012Metric_Pad1.18x1.45mm_HandSolder
J3: DRIVE_GND; Pin_D1.3mm_L11.0mm
J4: DRIVE_5V; Pin_D1.3mm_L11.0mm
J5: 3.3V; Pin_D1.3mm_L11.0mm

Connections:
3.3V: J5.1; also elsewhere on the board
CURRENT_SENSE_OUT: A1.9 (IS_1); also elsewhere on the board
CURRENT_SIGN_OUT: A1.10 (IS_2); also elsewhere on the board
DRIVE_5V: C1.1, C2.1, C3.1, J4.1; also elsewhere on the board
DRIVE_GND: C1.2, C2.2, C3.2, J3.1; also elsewhere on the board
DRIVE_INPUT: A1.19 (D4); also elsewhere on the board
D_5V: A1.5 (5V); also elsewhere on the board
D_GND: A1.7 (GND); also elsewhere on the board
LOAD_INPUT: A1.27 (INH_1), A1.28 (INH_2); also elsewhere on the board
STUDENT_ENABLE: A1.20 (D5); also elsewhere on the board
STU_LED_1: A1.21 (D6); also elsewhere on the board
STU_LED_2: A1.22 (D7); also elsewhere on the board
STU_LED_3: A1.23 (D8); also elsewhere on the board
SUP_LED_1: A1.25 (D10); also elsewhere on the board
SUP_LED_2: A1.17 (D2); also elsewhere on the board
SUP_LED_3: A1.24 (D9); also elsewhere on the board

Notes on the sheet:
Capacitors to supply current to the Coil

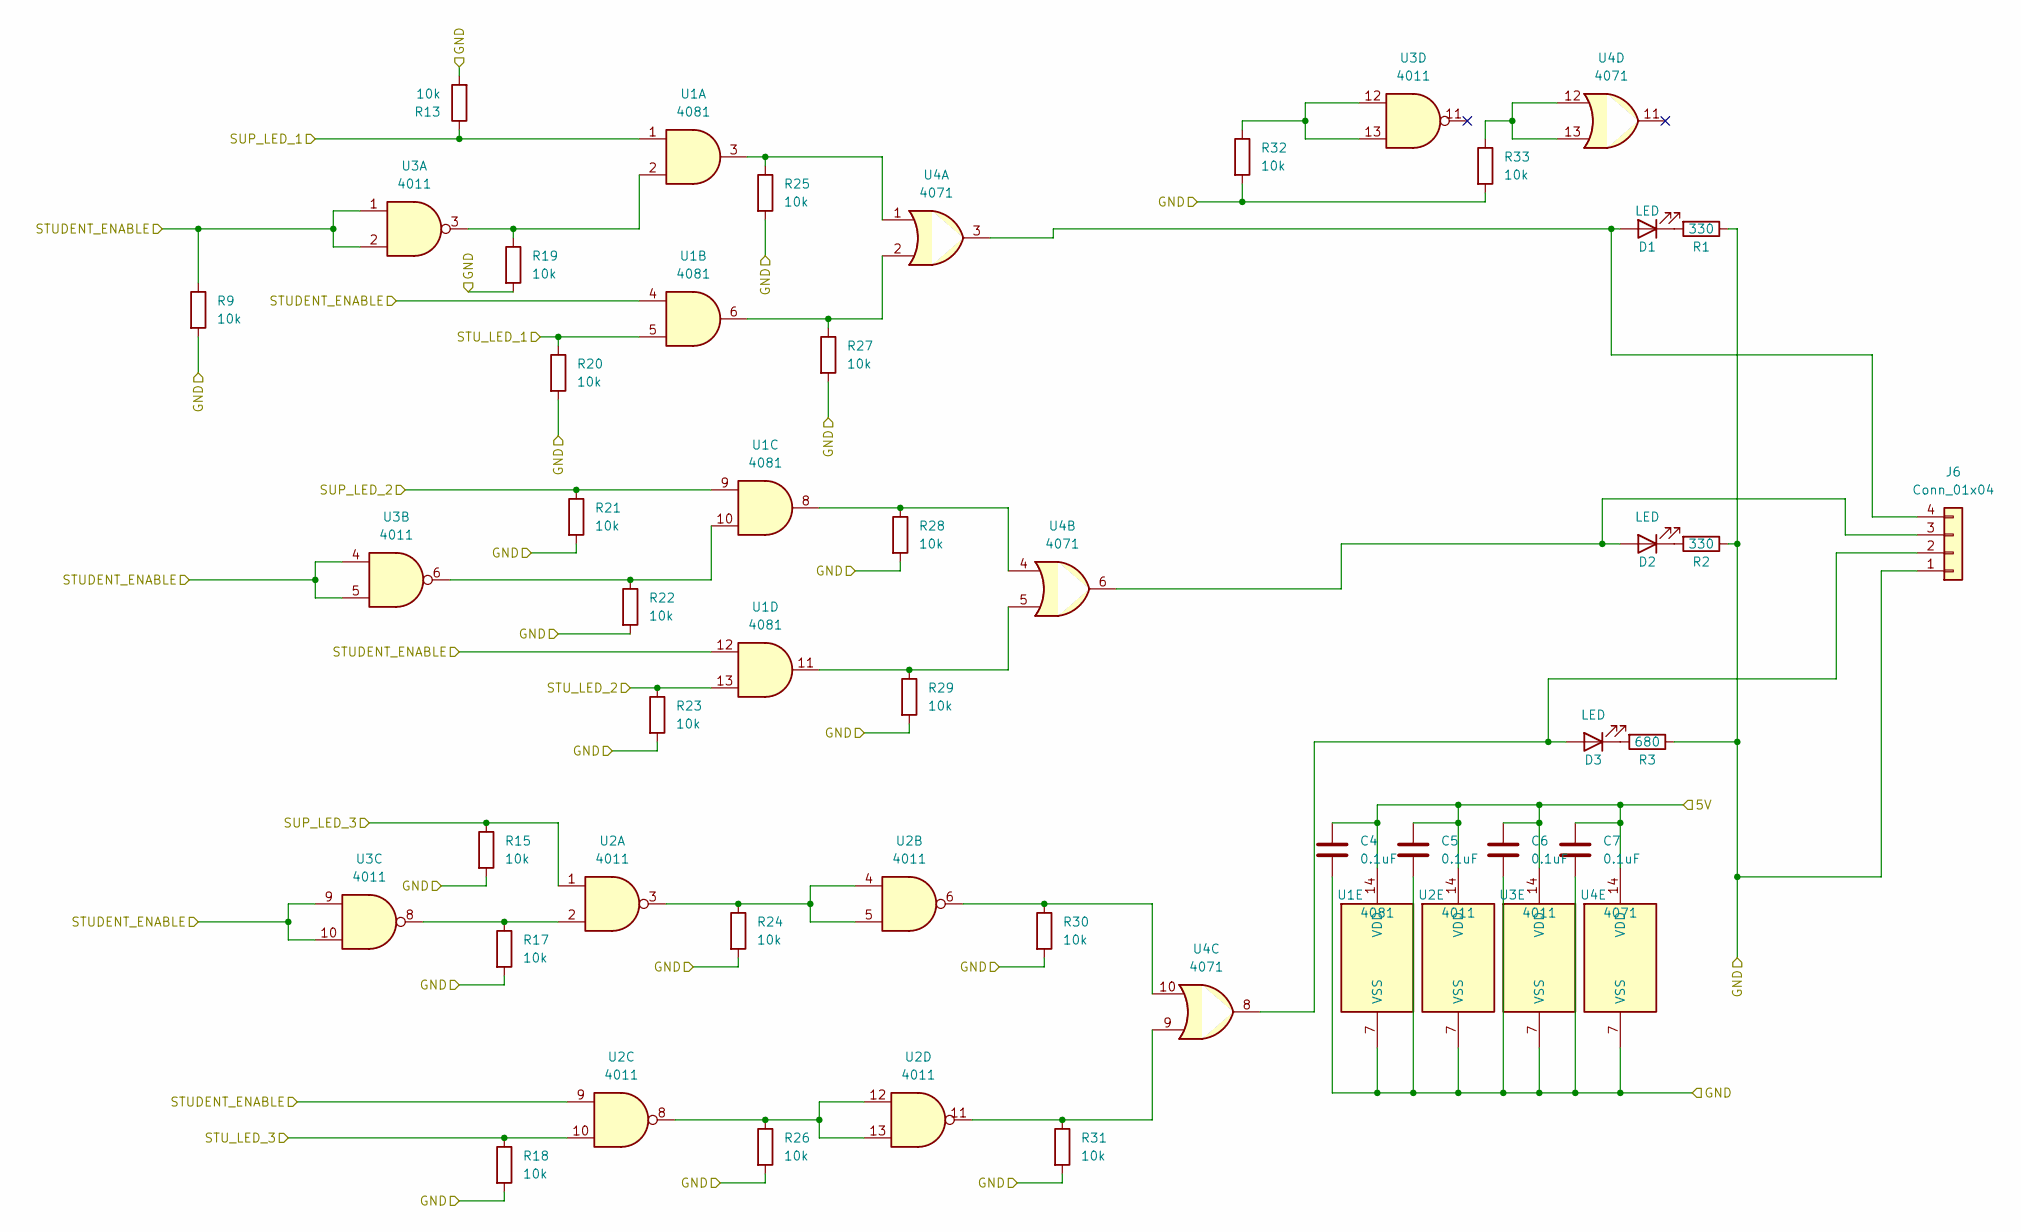
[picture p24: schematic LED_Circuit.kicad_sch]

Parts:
C4, C5, C6, C7: 0.1uF; C_0805_2012Metric_Pad1.18x1.45mm_HandSolder
D1, D2, D3: LED; LED_0805_2012Metric_Pad1.15x1.40mm_HandSolder
J6: Conn_01x04; PinHeader_1x04_P2.54mm_Vertical
R1, R2: 330; R_0805_2012Metric_Pad1.20x1.40mm_HandSolder
R3: 680; R_0805_2012Metric_Pad1.20x1.40mm_HandSolder
R9, R13, R15, R17, R18, R19, R20, R21, R22, R23, R24, R25, R26, R27, R28, R29, R30, R31, R32, R33: 10k; R_0805_2012Metric_Pad1.20x1.40mm_HandSolder
U1: 4081; SOIC127P600X175-14N
U2, U3: 4011; SOIC127P600X175-14N
U4: 4071; SOIC127P600X175-14N

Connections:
D_5V: C4.1, C5.1, C6.1, C7.1, U1.14 (VDD), U2.14 (VDD), U3.14 (VDD), U4.14 (VDD); also elsewhere on the board
D_GND: C4.2, C5.2, C6.2, C7.2, J6.1, R1.1, R2.1, R3.1, R9.2, R13.2, R15.2, R17.2, R18.2, R19.2, R20.2, R21.2, R22.2, R23.2, R24.2, R25.2, R26.2, R27.2, R28.2, R29.2, R30.2, R31.2, R32.2, R33.2, U1.7 (VSS), U2.7 (VSS), U3.7 (VSS), U4.7 (VSS); also elsewhere on the board
unnamed: D1.1 (K), R1.2
unnamed: D1.2 (A), J6.4, U4.3
unnamed: D2.1 (K), R2.2
unnamed: D2.2 (A), J6.3, U4.6
unnamed: D3.1 (K), R3.2
unnamed: D3.2 (A), J6.2, U4.8
unnamed: R17.1, U2.2, U3.8
unnamed: R19.1, U1.2, U3.3
unnamed: R22.1, U1.10, U3.6
unnamed: R24.1, U2.3, U2.4, U2.5
unnamed: R25.1, U1.3, U4.1
unnamed: R26.1, U2.8, U2.12, U2.13
unnamed: R27.1, U1.6, U4.2
unnamed: R28.1, U1.8, U4.4
unnamed: R29.1, U1.11, U4.5
unnamed: R30.1, U2.6, U4.10
unnamed: R31.1, U2.11, U4.9
unnamed: R32.1, U3.12, U3.13
unnamed: R33.1, U4.12, U4.13
STUDENT_ENABLE: R9.1, U1.4, U1.12, U2.9, U3.1, U3.2, U3.4, U3.5, U3.9, U3.10; also elsewhere on the board
STU_LED_1: R20.1, U1.5; also elsewhere on the board
STU_LED_2: R23.1, U1.13; also elsewhere on the board
STU_LED_3: R18.1, U2.10; also elsewhere on the board
SUP_LED_1: R13.1, U1.1; also elsewhere on the board
SUP_LED_2: R21.1, U1.9; also elsewhere on the board
SUP_LED_3: R15.1, U2.1; also elsewhere on the board


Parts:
Q3, Q4: BSS138; SOT-23
R10, R11, R12, R14: 10k; R_0805_2012Metric_Pad1.20x1.40mm_HandSolder

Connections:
3.3V: Q3.1 (G), Q4.1 (G), R10.1, R12.1; also elsewhere on the board
DRIVE: Q3.3 (D), R11.2; also elsewhere on the board
DRIVE_5V: R11.1, R14.1; also elsewhere on the board
DRIVE_INPUT: Q3.2 (S), R10.2; also elsewhere on the board
LOAD: Q4.3 (D), R14.2; also elsewhere on the board
LOAD_INPUT: Q4.2 (S), R12.2; also elsewhere on the board


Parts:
C9: 0.1uF; C_0805_2012Metric_Pad1.18x1.45mm_HandSolder
D4: 1N4002; D_T-1_P5.08mm_Horizontal
IC1: MAX9928FAUA+; SOP65P490X110-8N; Manufacturer_Part_Number MAX9928FAUA+; Mouser Part Number 700-MAX9928FAUA
J2: Coil; RSPROPenduinoTerminal
JP1: Shunt Bypass; SolderJumper-2_P1.3mm_Open_Pad1.0x1.5mm
NT1, NT2, NT3: NetTie_2; NetTie-2_SMD_Pad0.5mm
Q1: BC858W; SOT-23
Q2: BD911; SOT-23
R4, R5: 2k2; R_0805_2012Metric_Pad1.20x1.40mm_HandSolder
R7: 10R; R_0805_2012Metric_Pad1.20x1.40mm_HandSolder

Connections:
CURRENT_SENSE_OUT: IC1.8 (OUT); also elsewhere on the board
CURRENT_SIGN_OUT: IC1.2 (SIGN); also elsewhere on the board
DRIVE_5V: C9.1, NT2.2, Q1.2 (E); also elsewhere on the board
DRIVE_GND: C9.2, D4.1 (A), J2.1, NT3.2, Q2.3 (E); also elsewhere on the board
DRIVE_OUT: R4.2; also elsewhere on the board
LOAD_OUT: R5.2; also elsewhere on the board
unnamed: D4.2 (K), IC1.1 (RS-), JP1.1 (A), Q1.3 (C), Q2.2 (C), R7.1
unnamed: IC1.3 (RS+), NT1.2
unnamed: IC1.6 (VCC), NT2.1
unnamed: IC1.7 (GND), NT3.1
unnamed: J2.2, JP1.2 (B), NT1.1, R7.2
unnamed: Q1.1 (B), R4.1
unnamed: Q2.1 (B), R5.1

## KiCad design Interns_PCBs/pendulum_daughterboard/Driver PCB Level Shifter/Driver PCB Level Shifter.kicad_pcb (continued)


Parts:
C8: 100nF; C_0805_2012Metric_Pad1.18x1.45mm_HandSolder
D5: LED; LED_0805_2012Metric_Pad1.15x1.40mm_HandSolder
J1: AVR-ISP-6; PinHeader_2x03_P2.54mm_Vertical
R6: 100k; R_0805_2012Metric_Pad1.20x1.40mm_HandSolder
R8: 680; R_0805_2012Metric_Pad1.20x1.40mm_HandSolder
SW1: SW_Push; 13019319
U5: ATtiny85-20S; SOIC-8W_5.3x5.3mm_P1.27mm

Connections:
DRIVE: J1.3 (SCK), U5.7 (PB2); also elsewhere on the board
DRIVE_5V: C8.1, J1.2 (VCC), R6.2, U5.8 (VCC); also elsewhere on the board
DRIVE_GND: C8.2, D5.1 (K), J1.6 (GND), SW1.1, U5.4 (GND); also elsewhere on the board
DRIVE_OUT: U5.3 (XTAL2/PB4); also elsewhere on the board
LOAD: J1.1 (MISO), U5.6 (PB1); also elsewhere on the board
LOAD_OUT: U5.2 (XTAL1/PB3); also elsewhere on the board
unnamed: D5.2 (A), R8.2
unnamed: J1.4 (MOSI), R8.1, U5.5 (AREF/PB0)
unnamed: J1.5 (~RST), R6.1, SW1.2, U5.1 (~RESET/PB5)


Board: 2 copper layers, 69.2 x 54.0 mm, 68 parts (0 on the bottom side), 49 nets.

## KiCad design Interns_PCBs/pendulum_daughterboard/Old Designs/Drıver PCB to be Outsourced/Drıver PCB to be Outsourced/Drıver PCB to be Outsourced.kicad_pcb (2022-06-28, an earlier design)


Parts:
A1: Infineon Motor Shield MOD; Infineon Motor Sheild hiddenPins
C1: 470u; C_Elec_8x10.2
C2: 10u; CP_Elec_3x5.3
C3: 0.1u; C_0805_2012Metric_Pad1.18x1.45mm_HandSolder
J5: DRIVE_GND; Pin_D1.3mm_L11.0mm
J7: DRIVE_5V_IN; Pin_D1.3mm_L11.0mm

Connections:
CURRENT_SENSE_OUT: A1.9 (IS_1); also elsewhere on the board
CURRENT_SIGN_OUT: A1.10 (IS_2); also elsewhere on the board
DRIVE_5V: C1.1, C2.1, C3.1, J7.1; also elsewhere on the board
DRIVE_GND: C1.2, C2.2, C3.2, J5.1; also elsewhere on the board
DRIVE_INPUT: A1.27 (INH_1), A1.28 (INH_2); also elsewhere on the board
D_5V: A1.5 (5V); also elsewhere on the board
D_GND: A1.7 (GND); also elsewhere on the board
LOAD_INPUT: A1.19 (D4); also elsewhere on the board
STUDENT_ENABLE: A1.20 (D5); also elsewhere on the board
STU_LED_1: A1.21 (D6); also elsewhere on the board
STU_LED_2: A1.22 (D7); also elsewhere on the board
STU_LED_3: A1.23 (D8); also elsewhere on the board
SUP_LED_1: A1.25 (D10); also elsewhere on the board
SUP_LED_2: A1.17 (D2); also elsewhere on the board
SUP_LED_3: A1.24 (D9); also elsewhere on the board

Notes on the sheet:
Capacitors to supply current to the Coil
To supply current to coil when switching.


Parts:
C4, C5, C6, C7: 100nF; C_0805_2012Metric_Pad1.18x1.45mm_HandSolder
D1, D2, D3: LED; LED_0805_2012Metric_Pad1.15x1.40mm_HandSolder
IC1: AND GATES; SOIC127P600X175-14N; Manufacturer_Part_Number CD74HC08QM96EP; Mouser Part Number 595-CD74HC08QM96EP
IC2: NAND (Used as AND); SOIC127P600X175-14N; Manufacturer_Part_Number MC74ACT00DG; Mouser Part Number 863-MC74ACT00DG
IC3: NAND (Used as Inverter); SOIC127P600X175-14N; Manufacturer_Part_Number MC74ACT00DG; Mouser Part Number 863-MC74ACT00DG
IC4: OR; SOIC127P600X175-14N; Manufacturer_Part_Number MC74ACT00DG; Mouser Part Number 863-MC74ACT00DG
J4: Conn_01x04; PinHeader_1x04_P1.27mm_Vertical
R1, R2, R3: 120; R_0805_2012Metric_Pad1.20x1.40mm_HandSolder

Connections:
AND_STU_LED_1: IC1.8 (3Y), IC4.2 (B1)
AND_STU_LED_2: IC1.11 (4Y), IC4.5 (B2)
AND_STU_LED_3: IC2.11 (Y4), IC4.10 (B3)
AND_SUP_LED_1: IC1.3 (1Y), IC4.1 (A1)
AND_SUP_LED_2: IC1.6 (2Y), IC4.4 (A2)
AND_SUP_LED_3: IC2.6 (Y2), IC4.9 (A3)
D_5V: C4.1, C5.1, C6.1, C7.1, IC1.14 (VCC), IC2.14 (VCC), IC3.14 (VCC), IC4.14 (VCC); also elsewhere on the board
D_GND: C4.2, C5.2, C6.2, C7.2, IC1.7 (GND), IC2.7 (GND), IC3.7 (GND), IC4.7 (GND), J4.1, R1.1, R2.1, R3.1; also elsewhere on the board
INV_1: IC1.2 (1B), IC3.3 (Y1)
INV_2: IC1.5 (2B), IC3.6 (Y2)
INV_3: IC2.2 (B1), IC3.8 (Y3)
unnamed: D1.1 (K), R1.2
unnamed: D2.1 (K), R2.2
unnamed: D3.1 (K), R3.2
unnamed: IC2.3 (Y1), IC2.4 (A2), IC2.5 (B2)
unnamed: IC2.8 (Y3), IC2.12 (A4), IC2.13 (B4)
OR_OUT_1: D1.2 (A), IC4.3 (Y1), J4.4
OR_OUT_2: D2.2 (A), IC4.6 (Y2), J4.3
OR_OUT_3: D3.2 (A), IC4.8 (Y3), J4.2
STUDENT_ENABLE: IC1.10 (3B), IC1.13 (4B), IC2.10 (B3), IC3.1 (A1), IC3.2 (B1), IC3.4 (A2), IC3.5 (B2), IC3.9 (A3), IC3.10 (B3); also elsewhere on the board
STU_LED_1: IC1.9 (3A); also elsewhere on the board
STU_LED_2: IC1.12 (4A); also elsewhere on the board
STU_LED_3: IC2.9 (A3); also elsewhere on the board
SUP_LED_1: IC1.1 (1A); also elsewhere on the board
SUP_LED_2: IC1.4 (2A); also elsewhere on the board
SUP_LED_3: IC2.1 (A1); also elsewhere on the board


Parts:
C9: 0.1uF; C_0805_2012Metric_Pad1.18x1.45mm_HandSolder
D4: 1N4002; D_T-1_P5.08mm_Horizontal
IC5: MAX9928FAUA+; SOP65P490X110-8N; Manufacturer_Part_Number MAX9928FAUA+; Mouser Part Number 700-MAX9928FAUA
J2: Coil; RSPROPenduinoTerminal
JP1: Shunt Bypass; SolderJumper-2_P1.3mm_Open_Pad1.0x1.5mm
NT1: NetTie_2; NetTie-2_SMD_Pad0.5mm
Q1: BC557; SOT-23
Q2: BC547; SOT-23
R4, R5: 2k2; R_0805_2012Metric_Pad1.20x1.40mm_HandSolder
R7: 10R; R_0805_2012Metric_Pad1.20x1.40mm_HandSolder

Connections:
CURRENT_SENSE_OUT: IC5.8 (OUT); also elsewhere on the board
CURRENT_SIGN_OUT: IC5.2 (SIGN); also elsewhere on the board
DRIVE_5V: Q1.3 (E); also elsewhere on the board
DRIVE_GND: D4.1 (A), J2.1, Q2.3 (E); also elsewhere on the board
DRIVE_MCU: R4.2; also elsewhere on the board
D_5V: C9.1, NT1.1; also elsewhere on the board
D_GND: C9.2, IC5.7 (GND); also elsewhere on the board
LOAD_MCU: R5.2; also elsewhere on the board
unnamed: D4.2 (K), IC5.1 (RS-), JP1.1 (A), Q1.1 (C), Q2.1 (C), R7.1
unnamed: IC5.3 (RS+), J2.2, JP1.2 (B), R7.2
unnamed: IC5.6 (VCC), NT1.2
unnamed: Q1.2 (B), R4.1
unnamed: Q2.2 (B), R5.1


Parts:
C8: 100nF; C_0805_2012Metric_Pad1.18x1.45mm_HandSolder
J1: AVR-ISP-6; PinHeader_2x03_P2.00mm_Vertical
R6: 100k; R_0805_2012Metric_Pad1.20x1.40mm_HandSolder
SW1: SW_Push; 13019319
U10: ATtiny85-20S; SOIC-8W_5.3x5.3mm_P1.27mm

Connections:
DRIVE_INPUT: J1.3 (SCK), U10.7 (PB2); also elsewhere on the board
DRIVE_MCU: U10.3 (XTAL2/PB4); also elsewhere on the board
D_5V: C8.1, J1.2 (VCC), R6.2, U10.8 (VCC); also elsewhere on the board
D_GND: C8.2, J1.6 (GND), SW1.1, U10.4 (GND); also elsewhere on the board
LOAD_INPUT: J1.1 (MISO), U10.6 (PB1); also elsewhere on the board
LOAD_MCU: U10.2 (XTAL1/PB3); also elsewhere on the board
unnamed: J1.4 (MOSI), U10.5 (AREF/PB0)
unnamed: J1.5 (~RST), R6.1, SW1.2, U10.1 (~RESET/PB5)


Board: 2 copper layers, 69.2 x 54.0 mm, 37 parts (0 on the bottom side), 41 nets.

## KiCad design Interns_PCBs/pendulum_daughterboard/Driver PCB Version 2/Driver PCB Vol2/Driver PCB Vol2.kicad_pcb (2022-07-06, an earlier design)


Board: 2 copper layers, 69.2 x 54.0 mm, 78 parts (0 on the bottom side), 72 nets.

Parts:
A1: Infineon Motor Shield MOD; Infineon Motor Sheild hiddenPins
C1: 470u; C_Elec_8x10.2
C2: 10u; CP_Elec_3x5.3
C3: 0.1u; C_0805_2012Metric_Pad1.18x1.45mm_HandSolder
C4, C5, C6, C7, C9: 0.1uF; C_0805_2012Metric_Pad1.18x1.45mm_HandSolder
C8: 100nF; C_0805_2012Metric_Pad1.18x1.45mm_HandSolder
D1, D2, D3, D5: LED; LED_0805_2012Metric_Pad1.15x1.40mm_HandSolder
D4: 1N4002; D_T-1_P5.08mm_Horizontal
IC5: MAX9928FAUA+; SOP65P490X110-8N
J1: AVR-ISP-6; PinHeader_2x03_P2.54mm_Vertical
J2: Coil; RSPROPenduinoTerminal
J4: Conn_01x04; PinHeader_1x04_P2.54mm_Vertical
J5: DRIVE_GND; Pin_D1.3mm_L11.0mm
J7: DRIVE_5V_IN; Pin_D1.3mm_L11.0mm
JP1: Shunt Bypass; SolderJumper-2_P1.3mm_Open_Pad1.0x1.5mm
NT1, NT2, NT3, NT4, NT5, NT6: NetTie_2; NetTie-2_SMD_Pad0.5mm
Q1: BC557; SOT-23
Q2: BC547; SOT-23
R1, R2: 330; R_0805_2012Metric_Pad1.20x1.40mm_HandSolder
R3, R8: 680; R_0805_2012Metric_Pad1.20x1.40mm_HandSolder
R4, R5: 2k2; R_0805_2012Metric_Pad1.20x1.40mm_HandSolder
R6: 100k; R_0805_2012Metric_Pad1.20x1.40mm_HandSolder
R7: 10R; R_0805_2012Metric_Pad1.20x1.40mm_HandSolder
R9, R10, R11, R12, R13, R14, R15, R16, R17, R18, R19, R20, R21, R22, R23, R24, R25, R26, R27, R28, R29, R30, R31: 480R; R_0805_2012Metric_Pad1.20x1.40mm_HandSolder
R32, R33, R34, R35, R36, R37, R38, R39, R40: 10kR; R_0805_2012Metric_Pad1.20x1.40mm_HandSolder
R41, R42: 480; R_0805_2012Metric_Pad1.20x1.40mm_HandSolder
SW1: SW_Push; 13019319
U1: 4081; SOIC127P600X175-14N
U2, U3: 4011; SOIC127P600X175-14N
U4: 4071; SOIC127P600X175-14N
U10: ATtiny85-20S; SOIC-8W_5.3x5.3mm_P1.27mm

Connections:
CURRENT_SENSE_OUT: A1.9 (IS_1), NT6.2
CURRENT_SIGN_OUT: A1.10 (IS_2), NT3.1
DRIVE_5V: C1.1, C2.1, C3.1, J7.1, Q1.3 (E)
DRIVE_GND: C1.2, C2.2, C3.2, D4.1 (A), J2.1, J5.1, Q2.3 (E)
DRIVE_INPUT: A1.27 (INH_1), A1.28 (INH_2), R33.2, R41.1
DRIVE_OUT: R4.2, U10.3 (XTAL2/PB4)
D_5V: A1.5 (5V), C4.1, C5.1, C6.1, C7.1, C8.1, C9.1, J1.2 (VCC), NT1.2, R6.2, U1.14 (VDD), U2.14 (VDD), U3.14 (VDD), U4.14 (VDD), U10.8 (VCC)
D_GND: A1.7 (GND), C4.2, C5.2, C6.2, C7.2, C8.2, C9.2, D5.2 (A), J1.6 (GND), J4.1, NT2.2, R1.1, R2.1, R3.1, R32.2, R33.1, R34.2, R35.2, R36.1, R37.2, R38.1, R39.2, R40.1, SW1.1, U1.7 (VSS), U2.7 (VSS), U3.7 (VSS), U4.7 (VSS), U10.4 (GND)
LOAD_INPUT: A1.19 (D4), R34.1, R42.2
LOAD_OUT: R5.2, U10.2 (XTAL1/PB3)
unnamed: D1.1 (K), R1.2
unnamed: D1.2 (A), J4.4, U4.3
unnamed: D2.1 (K), R2.2
unnamed: D2.2 (A), J4.3, U4.6
unnamed: D3.1 (K), R3.2
unnamed: D3.2 (A), J4.2, U4.10
unnamed: D4.2 (K), JP1.1 (A), NT5.1, Q1.1 (C), Q2.1 (C), R7.1
unnamed: D5.1 (K), R8.2
unnamed: IC5.1 (RS-), NT5.2
unnamed: IC5.2 (SIGN), NT3.2
unnamed: IC5.3 (RS+), NT4.2
unnamed: IC5.6 (VCC), NT1.1
unnamed: IC5.7 (GND), NT2.1
unnamed: IC5.8 (OUT), NT6.1
unnamed: J1.1 (MISO), R42.1, U10.6 (PB1)
unnamed: J1.3 (SCK), R41.2, U10.7 (PB2)
unnamed: J1.4 (MOSI), R8.1, U10.5 (AREF/PB0)
unnamed: J1.5 (~RST), R6.1, SW1.2, U10.1 (~RESET/PB5)
unnamed: J2.2, JP1.2 (B), NT4.1, R7.2
unnamed: Q1.2 (B), R4.1
unnamed: Q2.2 (B), R5.1
unnamed: R9.1, U3.1, U3.2
unnamed: R10.1, U1.1
unnamed: R11.1, U1.2
unnamed: R11.2, U3.3
unnamed: R12.1, U1.4
unnamed: R13.1, U1.5
unnamed: R14.1, U4.1
unnamed: R14.2, U1.3
unnamed: R15.1, U4.2
unnamed: R15.2, U1.6
unnamed: R16.1, U3.4, U3.5
unnamed: R17.1, U3.9, U3.10
unnamed: R18.1, U2.8
unnamed: R19.1, U2.9
unnamed: R20.1, U2.1
unnamed: R21.1, U2.2
unnamed: R21.2, U3.8
unnamed: R22.1, U1.12
unnamed: R23.1, U1.9
unnamed: R24.1, U1.10
unnamed: R24.2, U3.6
unnamed: R25.1, U1.13
unnamed: R26.1, U2.4, U2.5
unnamed: R26.2, U2.3
unnamed: R27.1, U2.12, U2.13
unnamed: R27.2, U2.10
unnamed: R28.1, U4.4
unnamed: R28.2, U1.8
unnamed: R29.1, U4.5
unnamed: R29.2, U1.11
unnamed: R30.1, U4.8
unnamed: R30.2, U2.6
unnamed: R31.1, U4.9
unnamed: R31.2, U2.11
STUDENT_ENABLE: A1.20 (D5), R9.2, R12.2, R16.2, R17.2, R18.2, R22.2, R35.1
STU_LED_1: A1.21 (D6), R13.2, R37.1
STU_LED_2: A1.22 (D7), R25.2, R39.1
STU_LED_3: A1.23 (D8), R19.2, R40.2
SUP_LED_1: A1.25 (D10), R10.2, R36.2
SUP_LED_2: A1.17 (D2), R23.2, R32.1
SUP_LED_3: A1.24 (D9), R20.2, R38.2

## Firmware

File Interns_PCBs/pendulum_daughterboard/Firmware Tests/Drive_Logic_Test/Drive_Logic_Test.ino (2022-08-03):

int STU_LED_1 = 6;
int STU_LED_2 = 7;
int STU_LED_3 = 8;
int SUP_LED_1 = 10;
int SUP_LED_2 = 2;
int SUP_LED_3 = 9;
int STU_ENABLE = 5;
int DRIVE_IN = 12;
int LOAD_IN = 4;

void setup() {
  // put your setup code here, to run once:
  pinMode (STU_LED_1, OUTPUT);
  pinMode (STU_LED_2, OUTPUT);
  pinMode (STU_LED_3, OUTPUT);
  pinMode (SUP_LED_1, OUTPUT);
  pinMode (SUP_LED_2, OUTPUT);
  pinMode (SUP_LED_3, OUTPUT);
  pinMode (STU_ENABLE, OUTPUT);
  pinMode (DRIVE_IN, OUTPUT);
  pinMode (LOAD_IN, OUTPUT);


}

void loop() {
  // put your main code here, to run repeatedly:

 digitalWrite (DRIVE_IN, LOW);
 digitalWrite (LOAD_IN, LOW);

 if (digitalRead(DRIVE_IN) == LOW  && digitalRead(LOAD_IN) == LOW)
  {
    digitalWrite(SUP_LED_1, HIGH);
  }

  if ( digitalRead(DRIVE_IN) == HIGH  && digitalRead(LOAD_IN) == LOW)
  {
    digitalWrite(SUP_LED_2, HIGH);
  }

  if (digitalRead(DRIVE_IN) == LOW  && digitalRead(LOAD_IN) == HIGH)
  {
    digitalWrite(SUP_LED_3, HIGH);
  }

  
  if (digitalRead(DRIVE_IN) == HIGH  && digitalRead(LOAD_IN) == HIGH)
  {
    digitalWrite(SUP_LED_3, HIGH);
    digitalWrite(SUP_LED_1, HIGH);
    digitalWrite(SUP_LED_2, HIGH);
  }


}

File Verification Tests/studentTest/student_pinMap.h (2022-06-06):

/*  #Remote Labs Supervisor MCU PinMap
*   
*	Imogen Heard
*	25/05/2022
*
*/

#ifndef supervisor_pinMap_h
#define supervisor_pinMap_h




// Arduino Compatable Pins


#define ENCODER_B				    2
#define ENCODER_A				    3
#define ENCODER_INDEX		   	4
#define PIXEL_DATA				  5
#define STEPP_STEP 				  6
#define DC_MOTOR_DIR2			  7
#define LATCH				      	8
#define SERVO_1					    9
#define DC_MOTOR_PWM		   	10
#define	MOSI					      11
#define DC_MOTOR_DIR1			  12
#define SCK						      13
#define SPARE_1					    15     // <- not the same as Supervisor
#define LIMIT_1					    18
#define STEPP_FLT			    	19

#define SPARE_2	    				A2
#define THERMO				    	A3
#define DC_MOTOR_IS2	  		A6
#define DC_MOTOR_IS1	  		A7


// Shift Register Pins (Needs shiftRegister.h to validate)

#define DC_MOTOR_EN			  	Q0
#define SHIFT_1	    				Q1
#define SHIFT_2			    		Q2
#define SHIFT_3			    		Q3
#define STEPP_DIR			    	Q4
#define STEPP_EN	    			Q5
#define STEPP_RST	    			Q6
#define SHIFT_REG_7		   		Q7












#endif

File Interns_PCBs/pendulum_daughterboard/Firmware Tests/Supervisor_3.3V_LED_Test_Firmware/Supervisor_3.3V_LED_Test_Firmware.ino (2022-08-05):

#include "supervisor_pinMap.h"

#include "shiftRegister.h"

//Assigning names for the function of the pendulum board

#define SUP_LED_1 DC_MOTOR_DIR1

#define SUP_LED_2 DC_MOTOR_DIR2

#define SUP_LED_3 SERVO_1

#define STU_ENABLE STUDENT_M_EN

#define DRIVE DC_MOTOR_EN

#define LOAD STEPP_STEP

shiftRegister shiftReg(MOSI, SCK, LATCH);



void setup() {
  // put your setup code here, to run once:

  pinMode (SUP_LED_1, OUTPUT);
  pinMode (SUP_LED_2, OUTPUT);
  pinMode (SUP_LED_3, OUTPUT);
  pinMode (STU_ENABLE, OUTPUT);
  pinMode (DRIVE, OUTPUT);
  pinMode (LOAD, OUTPUT);
  shiftReg.begin();


//flashLED();
}



void loop() {
//Initially setting all the pins low


 shiftReg.shiftWrite(DRIVE, LOW);  
 digitalWrite (LOAD, LOW); 
 shiftReg.shiftWrite(STU_ENABLE, LOW);
 digitalWrite (SUP_LED_1, HIGH);
 digitalWrite (SUP_LED_2, HIGH);
 digitalWrite (SUP_LED_3, HIGH);

  // Trying to turn the pins on without enable

  //delay(3000);
//  digitalWrite (STU_LED_1, HIGH);
 // delay(1000);
  //digitalWrite (STU_LED_1,  LOW);
  //digitalWrite (STU_LED_2, HIGH);
 // delay(1000);
  //digitalWrite (STU_LED_2, LOW);
  //digitalWrite (STU_LED_3, HIGH);
  //delay(1000);
  //digitalWrite (STU_LED_3, LOW);
  //digitalWrite (SUP_LED_1, HIGH);
  //delay(1000);
  //digitalWrite (SUP_LED_1, LOW);
  //digitalWrite (SUP_LED_2, HIGH);
 // delay(1000);
  //digitalWrite (SUP_LED_2, LOW);
 // digitalWrite (SUP_LED_3, HIGH);

  // Trying to turn the pins on with enable
 // delay(1000);
 // digitalWrite (STU_ENABLE, HIGH);
 // delay(1000);
 // digitalWrite (SUP_LED_3, LOW);
//  digitalWrite (STU_LED_1, HIGH);
 // delay(1000);
//  digitalWrite (STU_LED_1,  LOW);
//  digitalWrite (STU_LED_2, HIGH);
//  delay(1000);
 // digitalWrite (STU_LED_2, LOW);
 // digitalWrite (STU_LED_3, HIGH);
 // delay(1000);
 // digitalWrite (STU_LED_3, LOW);
 // digitalWrite (SUP_LED_1, HIGH);
 // delay(1000);
 // digitalWrite (SUP_LED_1, LOW);
 // digitalWrite (SUP_LED_2, HIGH);
 // delay(1000);
 // digitalWrite (SUP_LED_2, LOW);
  //digitalWrite (SUP_LED_3, HIGH);



}


void flashLED() {
  int count = 6;
  while (count) {
    digitalWrite (SUP_LED_1, HIGH);
    delay(500);
    digitalWrite (SUP_LED_1,  LOW);
    delay(200);
    count--;
  }
}

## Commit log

2022-03-23 added kicad files
    [MCU_student.kicad_sch, MCU_supervisor.kicad_sch, RemoteLabs_supervisor_PCB.kicad_pcb, RemoteLabs_supervisor_PCB.kicad_sch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]
2022-03-23 updated requirements
    [MCU_student.kicad_sch, MCU_supervisor.kicad_sch, dc_motor_controller.kicad_sch, hardwired_logic.kicad_sch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]
2022-04-07 started working on schematic
    [RemoteLabs_supervisor_PCB.kicad_sch, dc_motor_controller.kicad_sch, output_logic.kicad_sch, sensor_distribution.kicad_sch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]
2022-04-08 Schematric work
    [RemoteLabs_supervisor_PCB.kicad_sch, analog_sensors.kicad_sch, analog_signal_buffers.kicad_sch, dc_motor_controller.kicad_sch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]
2022-04-18 adding test sketch
    [MCU_supervisor.kicad_sch, RemoteLabs_supervisor_PCB.kicad_sch, analog_sensors.kicad_sch, analog_signal_buffers.kicad_sch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]
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2022-04-21 Schematic Work
    [MCU_supervisor.kicad_sch, RemoteLabs_supervisor_PCB.kicad_sch, dc_motor_controller.kicad_sch, stepper_controller.kicad_sch]
2022-04-22 lunchtime backup
    [RemoteLabs_supervisor_PCB.kicad_sch, dc_motor_controller.kicad_sch, output_logic.kicad_sch]
2022-04-22 Circuit Design 85-90% complete
    [MCU_supervisor.kicad_sch, RemoteLabs_supervisor_PCB.kicad_sch, digital_signal_buffers.kicad_sch, output_logic.kicad_sch]
2022-04-25 nearing circut deisng complete
    [MCU_student.kicad_sch, MCU_supervisor.kicad_sch, RemoteLabs_supervisor_PCB.kicad_sch]
2022-04-26 V1.0 Circuit Design Complete
    [KiCad_Package_Tracker.xlsx, MCU_student.kicad_sch, MCU_supervisor.kicad_sch, RemoteLabs_supervisor_PCB.kicad_sch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]
2022-04-26 ERC checks run
    [MCU_student.kicad_sch, MCU_supervisor.kicad_sch, RemoteLabs_supervisor_PCB.kicad_sch, dc_motor_controller.kicad_sch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]
2022-04-27 Schematic reviewed
    [BOM_SUPERVISOR_REMOTELABS_INITIAL.xlsx, MCU_student.kicad_sch, MCU_supervisor.kicad_sch, RemoteLabs_supervisor_PCB.csv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]
2022-05-02 Finished BOM and purchasing
    [BOM_SUPERVISOR_REMOTELABS_INITIAL.xlsx, MCU_student.kicad_sch, MCU_supervisor.kicad_sch, RemoteLabs_supervisor_PCB.kicad_sch]
2022-05-03 Footprint Association Underway
    [BOM_SUPERVISOR_REMOTELABS_INITIAL.xlsx, MCU_student.kicad_sch, MCU_supervisor.kicad_sch, RemoteLabs_supervisor_PCB.kicad_sch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]
2022-05-05 Finished Ordering and stock control
    [BOM_Still to orderL.xlsx, RemoteLabs_supervisor_PCB clean.xlsm]
2022-05-05 Problems with power consumption
    Added additional power bus, annoying and expensive but best action
    [BOM_SUPERVISOR_REMOTELABS_INITIAL.xlsx, BOM_Still to orderL.xlsx, Current_Power_and_Trace_Calculator.xlsx, MCU_student.kicad_sch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]
2022-05-10 Footprint associations complete
    [Current_Power_and_Trace_Calculator.xlsx, MCU_student.kicad_sch, MCU_supervisor.kicad_sch, RemoteLabs_supervisor_PCB clean.xlsm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]
2022-05-11 Started PCB layout
    [Current_Power_and_Trace_Calculator.xlsx, MCU_student.kicad_sch, MCU_supervisor.kicad_sch, RemoteLabs_supervisor_PCB clean.xlsm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]
2022-05-12 PCB layout
    [ComplexClock.kicad_pcb, ComplexClock.kicad_sch, MCU_student.kicad_sch, MCU_supervisor.kicad_sch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]
2022-05-14 version one finished excluding net ties
    [RemoteLabs_supervisor_PCB.kicad_pcb, RemoteLabs_supervisor_PCB.kicad_sch, power_distribution.kicad_sch]
2022-05-14 created backup kicad folder
    [ComplexClock.kicad_pcb, ComplexClock.kicad_sch, MCU_student.kicad_sch, MCU_supervisor.kicad_sch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]
2022-05-14 routing board layout 2.0
    [RemoteLabs_supervisor_PCB.kicad_pcb, RemoteLabs_supervisor_PCB.kicad_sch, output_logic.kicad_sch]
2022-05-15 2 am save
    [RemoteLabs_supervisor_PCB.kicad_pcb]
2022-05-15 2:01 am save going to bed
    [RemoteLabs_supervisor_PCB.kicad_pcb]
2022-05-15 Version 2 PCB Layout
    [RemoteLabs_supervisor_PCB.kicad_pcb, RemoteLabs_supervisor_PCB.kicad_sch, power_distribution.kicad_sch]
2022-05-15 Board V2 Finished
    [RemoteLabs_supervisor_PCB.kicad_pcb]
2022-05-16 Added graphics and 3D model screenshots
    [RemoteLabs_supervisor_PCB.kicad_pcb]
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2022-05-16 Added fabrication outputs and organised folders
    [ComplexClock.kicad_pcb, ComplexClock.kicad_sch, MCU_student.kicad_sch, MCU_supervisor.kicad_sch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]
2022-05-25 Added documentation for testing
    Added pin declarations headers
    outlined requirements for test firmware for PCB verification
    [REMOTE_LABS_CONNECTOR_ORDERING.xlsx, Supervisor_PCB_PinMap.xlsx, parts wishlist.xlsx]
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2022-06-06 Test software mostly tested - awaiting hardware
    [RemoteLabs_supervisor_PCB.kicad_sch, digital_sensors.kicad_sch]
2022-06-09 added BOMs
    [RemoteLabs_supervisor_PCB SMD FABRICATION.xlsm, RemoteLabs_supervisor_PCB clean.xlsm, RemoteLabs_supervisor_PCB.csv]
2022-06-10 Edited PCB design for V1.1
    - Changed pin sizes for stepper motor
    - Change pin sizes for DC/DC Buck module.
    - In process of changing text to be readable by human beings
    [MCU_student.kicad_sch, MCU_supervisor.kicad_sch, RemoteLabs_supervisor_PCB.kicad_pcb, RemoteLabs_supervisor_PCB.kicad_sch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]
2022-06-13 Updated PCB for V1.1 see CHANGELOG
    Test software refinement
    [RemoteLabs_supervisor_PCB.kicad_pcb, RemoteLabs_supervisor_PCB.kicad_sch, digital_sensors.kicad_sch, power_distribution.kicad_sch]
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2022-06-14 Many Changes
    [RemoteLabs_supervisor_PCB.kicad_pcb]
2022-06-14 Updated some shite
    [RemoteLabs_supervisor_PCB.kicad_pcb]
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2022-06-21 Version 1.2 PCB
    [MCU_student.kicad_sch, MCU_supervisor.kicad_sch, RemoteLabs_supervisor_PCB-B_Cu.gbr, RemoteLabs_supervisor_PCB-B_Mask.gbr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]
2022-06-21 Added Pendulum Driver PCB Files
    [Driver PCB.kicad_pcb, Driver PCB.kicad_sch, LED_Circuit.kicad_sch, Microcontroller_Circuit_sch.kicad_sch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]
2022-06-22 Today's Progress on the PCB
    22/06/22
    [Current_detection.kicad_sch, Drive_Circuit.kicad_sch, Driver PCB.kicad_pcb, Driver PCB.kicad_sch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]
2022-06-23 changes
    11.50
    [Drive_Circuit.kicad_sch, Driver PCB.kicad_pcb, Driver PCB.kicad_sch, Microcontroller_Circuit_sch.kicad_sch]
2022-06-23 Changes to the PCB
    23/06/2022
    [Driver PCB.csv, Driver PCB.kicad_pcb, Driver PCB.kicad_sch]
2022-06-24 Penduino Daughterboard Update
    The complete design before checks.
    [Driver PCB.kicad_pcb, Driver PCB.kicad_sch]
2022-06-24 Penduino Board Update
    [Bill of Materials Penduino Daugterboard.xlsx, Driver PCB Generated BoM.csv, Driver PCB-B_Cu.gbr, Driver PCB-B_Mask.gbr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]
2022-06-24 Add PCB for RasPi Hat
    [RasPi_Hat.kicad_pcb, RasPi_Hat.kicad_sch, RasPi_Hat_BOM.csv]
2022-06-24 Fixed Silkscreen
    [RasPi_Hat.kicad_pcb]
2022-06-24 changed file structure
    [Bill of Materials Penduino Daugterboard.xlsx, Current_detection.kicad_sch, Drive_Circuit.kicad_sch, Driver PCB Generated BoM.csv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]
2022-06-24 Update Bill of Materials Penduino Daugterboard.xlsx
    [Bill of Materials Penduino Daugterboard.xlsx]
2022-06-24 Changed Diode
    [Drive_Circuit.kicad_sch, Driver PCB-B_Cu.gbr, Driver PCB-B_Mask.gbr, Driver PCB-B_Paste.gbr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]
2022-06-24 Added fabrication template for in house PCB production
    [Intern_PCB_FAB.kicad_pcb, Intern_PCB_FAB.kicad_sch, PCB_fabrication_template.kicad_pcb, RasPi_Hat.kicad_pcb]
2022-06-24 Changes with the Components
    [Bill of Materials Penduino Daugterboard.xlsx, Driver PCB.kicad_pcb, Driver PCB.kicad_sch]
2022-06-24 Friday Updates
    24/06/22
    [Bill of Materials Penduino Daugterboard.xlsx, Drive_Circuit.kicad_sch, Driver PCB.kicad_pcb, Driver PCB.kicad_sch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]
2022-06-25 New Design for Outsourcıng
    Added a new design that can be outsourced from a manufacturer. It includes smaller track widths, clearences, via diameter and hole size. Making the design more compact.
    [Current_detection.kicad_sch, Drive_Circuit.kicad_sch, Driver PCB Generated BoM.csv, Drıver PCB to be Outsourced-B_Cu.gbr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]
2022-06-30 Fabrication Files
    [Intern_PCB_FAB-B_Cu.gbr, Intern_PCB_FAB-Edge_Cuts.gbr, Intern_PCB_FAB-F_Cu.gbr, Intern_PCB_FAB-F_Silkscreen.gbr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]
2022-07-01 01/07 UPDATES
    [Bill of Materials Penduino Daugterboard.xlsx, Driver PCB.kicad_pcb, Driver PCB.kicad_sch, Intern_PCB_FAB-B_Cu.gbr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]
2022-07-04 Changed Logic
    [Driver PCB.kicad_sch, LED_Circuit.kicad_sch]
2022-07-05 Pull down and Current Limiting Resistors
    [Driver PCB.kicad_pcb, Driver PCB.kicad_sch, LED_Circuit.kicad_sch, Microcontroller_Circuit_sch.kicad_sch]
2022-07-06 Pendulum PCB Version 2
    [Current_detection.kicad_sch, Drive_Circuit.kicad_sch, Driver PCB Generated BoM.csv, Driver PCB Vol2-B_Cu.gbr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]
2022-07-06 One Connection Left
    [Driver PCB Vol2.kicad_pcb]
2022-07-07 attiny 85 pendulum logic
    [Driver PCB.kicad_pcb, Driver PCB.kicad_sch, LED_Circuit.kicad_sch]
2022-07-07 Pendulum Driver PCB Vol3
    With pull down resistors
    [Current_detection.kicad_sch, Drive_Circuit.kicad_sch, Driver PCB Generated BoM.csv, Driver PCB Vol2-B_Cu.gbr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]
2022-07-07 Added population BOM
    [RemoteLabs_supervisor_PCB.csv, RemoteLabs_supervisor_PCBV1.2.csv]
2022-07-11 Flipped Diode on schematic
    [Drive_Circuit.kicad_sch, LED_Circuit.kicad_sch, Microcontroller_Circuit_sch.kicad_sch]
2022-07-11 edited CSV
    [RemoteLabs_supervisor_PCBV1.2.csv]
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
